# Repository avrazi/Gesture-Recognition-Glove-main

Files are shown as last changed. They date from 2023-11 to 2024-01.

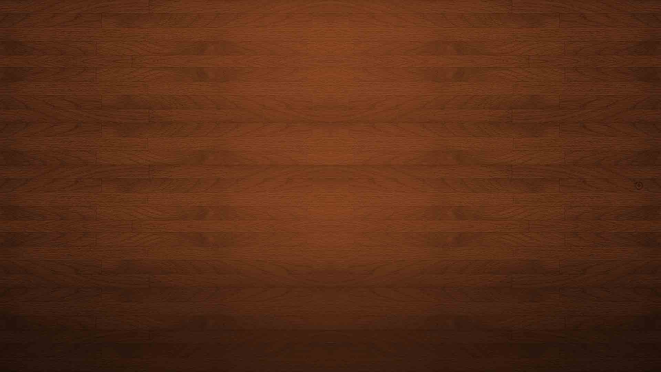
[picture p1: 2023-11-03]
Algorithm/src/wood-backgrounds-wallpapers.jpg

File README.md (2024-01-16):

# Gesture Recognition Glove

*A short intro before starting the article. To anyone who will find themselves reading through this project, please know that, being written around 2020-2021, the algorithm is most likely out-of-date, from the libraries to the dev board used. I've kept everything untouched since then just as some sort comparison for myself a long time ago. Hope it helps!*

***The whole prototype will require 5 flex sensors, a development board, an accelerometer,
gyroscope, and a battery shield.*** During the making of this prototype, a wearable glove will be created
that is **responsive, portable, and durable.** It will be able to translate sign language gestures into readable
form for hearing-impaired people by analysing the bend of the fingers and the position of the hand in
space, process it and send messages to the website. The project started by selecting a suitable
development board, a suitable power supply corresponding the voltage input of this controller, selecting
the right sensors, developing the firmware, designing the PCB and enclosure, and building the prototype.
The PCB will rest along with the battery shield onto a custom-made enclosure. This enclosure will rest
on the back of the hand of the user using a strap keep it tight with the hand and a buckle connecting both
ends of the strap. It will have two straps going on the specified holes. One will be resting above the
thumb and the other strap that connects with a buckle, on the wrist. This will lead for the entire prototype
to not be too close to the fingers, making it a suitable place to make the connection through the
connectors.

The focus of the demo prototype will be on reading and analysing hand movement. Since ASL’s gestures require an extensive range of motions, including rotation and complex arm movement, the algorithm of this prototype will have to be exceptionally well written. It will need to capture correct and consistent analog to digital data to have a precise definition for each value. To bring the proposed design as close as possible to becoming a viable product, there should be a certain required level of standards related to safety to follow. As with any electronic equipment, there is a risk of shorting wires, which can result in injury or fire. This means the points where wires are connected with the Flex Sensors will be fully insulated and the enclosure will have to cover most of the PCB and power supply. Sometimes between gestures, there are very subtle differences and minor changes, so this similarity can be read and
analysed from the glove as the same gesture. The complexity of ASL make it challenging to distinguish
and capture differences between gestures. This means the sensors should have a desired sensitivity and
linearity as well as a well-developed software algorithm that detects these subtle changes. In this case,
we were faced with two options on how to proceed and develop the algorithm. One could be using
machine learning, where the glove would be trained over time by performing the same gestures, or by
creating a dataset function holding if constraints with segments of values. With datasets one gesture
would have exact predetermined values for every sensor reading and would be true if those values would
be met. Deciding which method to choose, and what components to use, we had to make several research
on similar products done beforehand and learn from them.

## Block Diagram

Our next very important step would be to design the block diagram, which will be crucial in the
foundation to the realization of this prototype. The block diagram provides a detailed view and
instructions, making it much easier to understand how every component is related to each other. It is
comprised of the Power supply, Input information, Data processing unit, Data acquisition and the
Website. Starting from the main source of power, the Power supply block (see figure below). It consists of
the battery which supplies the gyroscope, accelerometer, flex sensors and development board. The power
supply in our case will give a +5V as input voltage that goes into the voltage regulator of development
board which will drop it to 3.3V. We can see that the red line represents the input voltage throughout the
circuit. It goes from the microcontroller to the voltage divider of the flex sensor and to that sensor, and
it also connects with the accelerometer and gyroscope module.

Flex sensors will be connected with the microcontroller through an ADC pin and the
accelerometer and gyroscope through a I2C pin. The input information block is where the hand gestures
performed are picked up from the sensors as analog data and fed into the controller. This part only holds
outside factors regarding the prototype. The data given to the controller is processed and analysed
through the algorithm and checked with many datasets. Datasets in our case are going to be numerous if
constraints that hold specific values for when a certain sensor reaches that value. If one of these
constraints if fulfilled, then the output information, which is just a String value, will sent to the opened
webpage through the built-in Wi-Fi module of our development board. From the feeding of the data to
the microprocessor and till the moment this data was sent, it’s called Data Processing Block. In the last
stages of the block diagram, the data sent to webpage, arrives, gets pulled from a function in the
algorithm and is displayed.

The website will display the word, phrase, number, or letter depending on what gesture was
performed from the user of the glove. The information will be displayed as a translated gesture, which
is the goal of our prototype. To get access to this website, the user will have to be connected into the
same Wi-Fi that the board is connected to. By entering this local IP address into a browser of our choice,
we will be directed into the webpage, making the whole process of interaction, simple and efficient. The
website will be sending and giving requests with the board constantly.



#### ***ESP32 Devkit V1***

The ESP32 DevKit V1 is one of the development boards created to evaluate the ESPWROOM-32 module. It is based on the ESP32 microcontroller that boasts Wi-Fi, Bluetooth, Ethernet,
and Low Power support all in a single chip. ESP32 is already integrated antenna and RF balun, power
amplifier, low-noise amplifiers, filters, and power management module. The entire solution takes up the
least amount of printed circuit board area. This board is used with 2.4 GHz dual-mode Wi-Fi and
Bluetooth chips by TSMC 40nm low power technology, power, and RF properties best, which is safe,
reliable, and scalable to a variety of applications. The internal flash of the ESP32 module is organized
in a single flash area with pages of 4096 bytes each. There exist two different layouts based on the
presence of BLE support. Power to the ESP32 DevKit v1 is supplied via the on-board USB Micro B
connector or directly via the “VIN” pin. The power source is selected automatically. The device can
operate on an external supply of 5 to 20 volts. If using more than 12V, the voltage regulator may overheat
and damage the device. The recommended range is 5 to 12 volts. The ESP32 DevKit V1 comes with a
serial-to-USB chip on board that allows programming and opening the UART of the ESP32 module. It
can be programmed in different programming environments like Arduino IDE, Espressif IDF (IoT
Development Framework), MicroPython, JavaScript, LUA.



##### **ADC Reading**

The development board supports 18 ADC channels. Each channel has 12 bits.
So, it has a good resolution. It can be used to measure analog voltage, current and any analog sensor
which provides output in the form of analog voltage. These ADCs can also be used in sleep mode for
lower power consumption. Each ADC channel has a resolution of 12 bits which is equal to: 3.3 / 4095
where 3.3V is a reference voltage and 4095 is minimum step by ADC. This value of 4095 is calculated
from the resolution number of every microcontroller. It is calculated as follows:
212 = 4095.
This means that when we read an analog input, its range may vary from 0 to 4095. Meaning that the
minimum voltage we can measure with these ADC channels is about 80 µV. Anything less than this will
be an error.
Ideally, we expected the ADC readings to have a linear behaviour while using these pins.
However, that is not true. While conducting research on this matter, the opposite was found to be true. We decided to perform an ADC linearity test. Four simple experiments by creating several voltage
dividers to read on. Source was at 3.3V output pin of the ESP32. Then we applied 3 different steps with
4.7k 1% tolerance resistors. These are the values measure with a multimeter:



The results of the Table above have been represented in the chart below. The readings
on the Table above, show when the voltage is at its maximum value, when it’s at ¾ of the maximum value, when
it’s at half and at ¼ of the maximum value. Our thought process was quite simple, as to divide both
voltage and ADC by 4 and have them as references. The most important part on this chart are the
beginning and the end of the characteristic. The behaviour means that our ESP32 cannot distinguish
3.3V from 3.2V. That means we will get the same values of 4095 from both voltages. The same happens
for a very low voltage of 0V to 0.1V. We are getting the same value of 0.



Another problem had arisen from our research that concerned the ADC pins. Specifically
speaking about ADC2 pins. Since our goal is to display our translated gestures using a website, then
the Wi-Fi of the board will be used. We learned that ADC2 pins cannot be used when Wi-Fi is being
used. This means, if we were to use the library of Wi-Fi, we would be getting an error at getting the
values from the ADC2 GPIO. The solution to this problem would be to only connect our flex sensors
with the ADC1 pins which would be GPIO36, GPIO39, GPIO34, GPIO35, GPIO32, and GPIO33.

##### **Voltage Regulator**

The ESP32 has a built-in low dropout voltage regulator chip called AMS1117. In our device,
its servers the function of a 5V to 3.3V linear voltage regulator, which means its main function is to
maintain a steady voltage. The AMS117 is an adjustable and fixed voltage regulator designed to
provide up to 1A output current and to operate down to 1V input-to-output differential. The dropout
voltage of the device is guaranteed maximum 1.3V, decreasing at lower load currents. Current limit is
set to minimize the stress under overload conditions on both the regulator and power source circuitry.
It has 3 fixed pins:

1. Ground
2. VOUT
3. VIN

From our research, we found that there are two versions for the AMS1117. A fixed version and
an adjustable one. Its application circuit is very simple. For the fixed version, it only needs two
capacitors and for the adjustable version only needs two resistors and two capacitors to work. Our
development board uses a fixed output voltage version. AMS1117 has six fixed versions: 1.2V, 1.8V,
2.5V, 2.85V, 3.3V and 5V. For us, we are using ASM1117-3.3, which possesses a
built-in protection against short circuit and thermal overloads. For instance, the circuity-wise thermal
protection will shut-down the linear regulator in case the junction temperature is above 165º C at the
sense point. It provides an output voltage of 3.3V by maximum output current of 1.5A and a maximum
input voltage of 12V. It guarantees a low dropout voltage (input-to-output) differential: VDROPOUT =
VIN – VOUT) of maximum 1.3V at the maximum output current of 1.5A. The dropout voltage decreases
at lower load currents and operates down to 1V dropout voltage. The on-chip trimming develops a
reference voltage of 1.25V between the output and the ground with a reference tolerance of 1.5%. This
means, we have more freedom to choose our power supply in regard to the input voltage required. We have included the electronic schematic of our voltage regulator circuit. It is comprised of 1
220Ώ resistance, 1 LED, 2 capacitors with the same value of 10µF.

##### **Power Consumption**

Since our goal is to build a portable and reliable prototype, we should consider how much does
the ESP32 consumes so we can have a better understand of its lifetime. ESP32 has different power modes
such as:

- Active Mode: The chip radio is powered on. The chip can receive, transmit, or listen.Page |36
- Modem-sleep Mode: The CPU is operational, and the clock is configurable. The WiFi/Bluetooth baseband and radio are disabled.
- Light-sleep Mode: The CPU is paused. The RTC memory and RTC peripherals, as well as
the ULP coprocessor are running. Any wake-up events will wake u the chip.
- Deep-sleep Mode: Only the RTC memory and RTC peripherals are powered on. Wi-Fi and
Bluetooth connection data are stored in the RTC memory. The ULP coprocessor is
functional.
- Hibernation Mode: The internal 8 MHz oscillator and ULP coprocessor are disabled. The
RTC recovery memory is powered down. Only one RTC timer on the slow clock and
certain RTC GPIOs are active.

While we want to have a website open during the whole time the device is on, and the ESP32
will be constantly communicating with the website, the power mode will be stated as ‘Active’. To have a better understanding about the development boards power consumption in an Active
Mode, we will be including a table displaying the RF Power-Consumption Specifications, from the ESP32 DevKit V1 documentation. We can approximate that our power consumption would be 240 mA, considering that we must
keep the development board and website communicating constantly to update the data. The formula to
find the battery life is as follows:
Battery Life (h) = Battery Capacity (mAh) / Device consumption (mA)
For example, if we were to have a battery with the capacity of 2000 mAh, and our maximum
consumption, in ideal conditions, we would have the device running for 8 hours and 19 minutes straight
without interruptions, which is enough for our project.

### Development Board

Regarding the power supply, a suitable battery was searched for to match the input voltage of the
chosen development board. As said before, our ESP32 requires an input voltage of 5V to 12V, so any
battery that has that output is enough for our project. We will be conducting research for rechargeable
battery options because we would like for the lifetime of the prototype being turn on to be as much as
possible without changing the battery. 

Three most common rechargeable battery types include NickelCadmium (NiCd), Nickel-Metal-Hydride (NiMH), and Lithium Polymer (LiPo). Each of these is a good
choice for projects and they all have their benefits and drawbacks. Nickel-Cadmium batteries have a
very high cycle count, and they are typically the cheapest of the three options. However, this type of
battery has a relatively low energy density, so they offer less capacity per cell than the other two types.
On the flip side, NiCd batteries can often deliver very high currents, which makes them perfect for power
tools. Note that NiCd batteries contain toxic heavy metals, which makes them more difficult to recycle.Page |38
Nickel-Metal-Hydride batteries are like NiCd cells. However, NiMH batteries offer an improvement in
capacity over NiCd batteries. One major drawback of NiMH cells is their high self-discharge rate. Li-Po
and Li-Ion batteries have a significantly higher energy density compared to typical NiMH and NiCd
cells. However, this benefit also means that you usually pay more for Li-Po and Li-Ion batteries. Besides
the increased price, lithium batteries always require monitoring by a battery management system, as
these batteries are sensitive to improper handling. Note that Li-Po batteries come in various shapes and
packages, of which some can be very flat. This makes Li-Po cells perfect for handheld devices such as
modern smartphones. Li-Ion batteries often come in larger sizes and are typically used in applications
where size isn’t critical. Note that there is not a single type of Li-Ion or Li-Po battery. Instead, the
category of lithium batteries comprises a whole range of different chemical formulations that all have
their very own pros, cons, and recommended applications.

In our case, a Li-Ion was chosen because they can be recharged many times and are quite stable
and efficient. They tend to have a higher energy density, voltage capacity and lower self-discharge rate
than other rechargeable batteries. This makes for better power efficiency as a single cell has longer
charge retention than other battery types. For the battery to be included and connected with the rest of
the prototype, it should be connected in a certain way. Either through connecting the VIN and GND pins
of the development board or through USB. As mentioned above, our chosen board has a micro-USB
type ‘B’ female. To have a much consistent connection and reliable to connect and disconnect, it was
decided to use a battery shield which will have an USB to make the connection with our board. The size
of this shield should be able to be held on the back of the hand of the user and it should have the option
of being rechargeable. The power supply’s purpose will be simple. It will be connected through USB
type A with the development board with the right input voltage. Since the development board requires
an input voltage of 5 V and has an operational voltage of 3.3V, it will be supplied the exact amount. The
battery shield chosen is the 18650 Battery shield (V3). It was considered for multiple reasons. This shield
is a cheap and portable power supply that can accommodate an ‘unprotected’ single-cell lithium-ion
battery. It also includes a standard USB type ‘A’ female connector, one power on/off switch and a micro-USB
type ‘B’ female for recharging. Its key specifications are as follows:

• Battery charging input: 5V/500mA typical via micro-USB port

• Power supply output: Switched 5VDC via USB type ‘A’ port, 3x 5VDC (VDC= volts
to direct current) (up to 4A) connectors, and 3x3VDC (up to 1A)

• System status indicators: Battery charging and battery charged LEDs

• Battery protection mechanism: Battery overcharge and deep discharge

The background electronics are a clever blend of three requisite circuits a lithium-ion
battery charger circuitry, a battery protection circuitry, and a dc-dc boost converter circuitry. Refer to
the annotated image provided below to get a deep insight on the underlying electronics. In the shield,
the dc - dc boost converter chip is used to deliver 5VDC (4.99V) through the USB ‘A’ socket and 5V
male-header points, generated from the available 3.7V-4.2VDC Li-Ion battery output. The second
channel output, marked as 3V but 3.3V on the dot, is supplied by the parallel combination of three
positive voltage regulator chips. The 3.3VDC supply is derived from the 3.7V-4.2VDC Li-Ion battery
output (not from the 5VDC output)



This device is composed of many components. They will be described by declaring their component
initials which can be check at its Schematic.

- U9 WD01A = Li-Ion battery protection chip
- F1 8205A = Dual N-Channel MOSFET
- U2 TP4056E = Li-Ion battery charger chip
- U7 FP6298 = 4.5A current mode DC-DC boost converter chip
- U4, U5, U6 (XC6206) = Positive voltage regulator chip (3.3V)Page |40
- L1 Green LED = Battery done charging indicator
- L2 Red LED = Battery charging indicator
- S1, S2, S4 = Schottky Diodes



### Flex Sensor

Capturing the bend of the fingers could be done in very few ways. Judging from the research
conducted beforehand on similar projects, flex sensors proved to be a good and efficient way of
measuring the bend of the fingers. Our options regarding the decision on acquiring the right flex sensor
for our prototype were limited. Generally, there are 3 main types of flex sensors: Conductive ink-based
flex sensors, fibre optic flex sensors and capacitive flex sensors. The conductive ink-based flex sensors
are quite common for projects of this nature. Capacitive and fibre optic flex sensors can be used more inPage |41
industrial and professional equipment. Conductive ink-based flex sensors are unipolar sensors, which
means the change of resistance is true only if you bend it in one direction. Bending the sensor on the
other direction does not change its resistance. It uses conductive ink whose resistance varies when bent.
The ink may contain carbon or silver to make it conductive. The spacing between carbon particles are
lager when bent and close when straight which results in a change of resistance.
Regarding the purchasing options, there were only two. 2.2 inches and 4.5 inches flex sensors
were available. 

Five 4.5 inches flex sensors were purchased instead of the 2.2 inches because they better
match the length of the fingers. The main computing device is going to be used to configure input and
output pins for each sensor, setup a clock speed, configure communications with the ADC, configure
communications with I2C pins, control sensor data, and send valid data to a Wi-Fi module. Flex Sensors
will be manipulated in the algorithm to decide whether the finger will be closed, open or to determine
exact positions for them.

##### **Power Consumption**

Each Flex Sensor is treated as a variable resistor whose resistance increases which the sensors
bending. Each sensor constitutes a part of its own voltage divider circuit, whose output is processed
through one of the development board’s analog-to-digital converters. The voltage provided from the
controller will be changing because of how much the corresponding finger is bent, which can lead to
problems while using the device. More specifically speaking, if the flex sensor would be changing its
value, the voltage would do as well. To fix this issue, voltage dividers will be placed before the Flex
Sensors. Voltage divider’s purpose in this case is to supply analog voltage values from
divider central point where both two resistors are connected. Voltage dividers only divides power
supply voltage value in proportion of Resistors values. One resistor has fixed value other value is
changing. Imagine two values are equal. Then voltage will be divided by 2.



The flex sensors were measured using a multimeter to determine their values. We agreed to set
the resistance when the sensor is straight as 12.3kΏ and for when it’s bend at 180º, it’s 29kΏ. By
connecting the sensor to a voltage divider circuit, the resulting voltage can be calculated from the
formula:



So, if we wanted to find out the output voltage, taking the flex sensor when it is straight and the
power supply voltage of 3.3V, according to the formula, it would be equal to 1.47V and for when we
are calculating for when flex sensor is bent, we get 0.846V.



Now, to find the current consumption of each flex sensor we would use this formula:



We can see that the circuit consumes very little current making it an energy efficient circuit,
considering that the board will reach around 240mA as consumption. This makes the use of the 10kΏ a
good value to choose for the voltage divider.
Regarding the value of voltage that will serve as an indicator for us to know if the flex sensor has
been bent, we decided that bending the sensor 90º (see Figure 24). This means that we can calculating
the resistance at half-way to our maximum bend value of 180º. This resistance is equal to:

29000Ώ – 12300Ώ = 16700Ώ.
16700Ώ / 2 = 8350Ώ.
12300Ώ + 8350 Ώ= 20650Ώ

We can calculate the voltage of this threshold as follows:



From our results we can understand that the voltage of 1.07V will be understood as a bend in the
flex sensor with that value.

### Accelerometer and Gyroscope

Regarding both accelerometer and gyroscope, the idea was based on the solution in Review 1,
where the team was using a MPU6050 module which contained both an accelerometer module and a
gyroscope module. It combines a 3-axis gyroscope and a 3-axis accelerometer on the same silicon die
together with an onboard Digital Motion Processor (DMP) capable of processing complex 9-axis
algorithms. This will help us to measure acceleration, velocity, orientation, displacement, and many
other motions related parameter of the prototype. The price of this is 5.5€ which made it a very
reasonable and efficient option for the realization of our prototype. It is comprised of 5 pins, INT, SCL,
SDA, GND and VIN. 

The INT is the interrupt signal which is an optional pin to connect. It indicates that
data is available for MCU to read. SCL stands for Serial Clock and is used for providing clock pulse for
I2C communication. SDA means Serial Data and is used for transferring data through I2C
communication. VIN will provide the power for this module, can be +3V to +5V depending on the added
power supply. In our case, the power will supply 5V into the board. GND stand for ground and connected
the system to ground. The main features or the MPU6050 are:

• MEMS 3-axis accelerometer and 3-axis gyroscope values combined,
• Power Supply: 3-5V,Page |44
• Communication: I2C protocol,
• Built-in 16-bit ADC provides high accuracy,
• Built-in DMP provides high computational power,
• Built-in Temperature sensor.

A gyroscope to capture the orientation and the angular velocity of the hands. Gyroscope will prove
useful for certain gestures that will require rotary movement in space. Accelerometer will be used to
measure the acceleration of the hand, which will be useful for gestures of phrases or words that need
stretched movement of the hand in space.



## Schematic Diagram

The first step taken for the realisation on this prototype was to design the schematic by placing
the components on a simulated breadboard to have a clearer view of how everything would be connected.
This proved to be quite helpful as a step before placing the components a real breadboard and start
experimenting. was designed using Altium Designer. This would
prove very useful, because the schematic would be imported easily for the next step of creating the PCB
using the same software. In the schematic, we can see how the components are connected with each
other. The flex sensors are shows as variable resistors with the names of Flex 1, Flex 2, Flex 3, Flex 4,
and Flex 5. Each sensors had their resistances measured beforehand to decide their value without any
force put into. This proved an approximated value of 12kΏ. Each of these sensors is connected to their
own voltage divider. These resistances have been assigned a value of 10kΏ. Each flex sensor has been
connected to an ADC pin of the ESP32. These pins are GPIO34, GPIO 35, GPIO 33, GPIO 32 and
GPIO39. We can also see in the schematic design that the MPU6050 module is connected without
development board as well.



The ESP32 has 6 Analog-To-Digital pins assigned as ADC1 and 9 Analog-To-Digital pins
assigned as ADC2. Since our goal is to send the data gathered to an opened webpage, this means that
the flex sensors would be able to connect to ADC1 pins only. From the schematic, we can
also see that the MPU6050 module is connected with the board to the specified pins. In the Pinout Figure
of the ESP32, we can see that GPIO21 and GPIO22 have the following names assigned: I2C SDA and
I2C SCL respectively. Therefore, they are connected to the pins of the same names of the module. Every
VIN pin has been connected and so has the GND pins. It is displayed that the input voltage of the circuit
will be 3.3V as is the operating voltage of the development board. The 18650 battery in-use are the
18650 US18650VTC4 Li-Ion 3.7V 2100mAh 30A. 

The ESP32’s lifetime on battery power has not been
tested, but as an approximation it could last around 4 months without charging the battery. Since the
board will be awake, it will need to be on during the whole time. Our main objective is to enable the user
of the glove to be able to fully communicate with another person through the use of a website, which
will serve as a lobby where anyone can connect with. This website will be run on the development board
at the same time it is reading the sensor data. As long as the user of the glove has a mobile phone and
internet mobile data, it will make the communication much easier. They will be taken to a specific IPPage |47
address where this webpage is opened. This was an option we explored as a very efficient one, amongst
other options. We could have developed an easy-to-use mobile application that would’ve performed the
same tasks, but it opened the way to new problems. Such as for what reason would someone download
this app, taking into consideration the chances a person has to meet someone with a hearing impairment.
Even if they did, it would’ve made it more difficult to get the message across to download it in order to
communicate. How would someone know the existence of this app? What if in an extreme situation,
there was a need for the interaction of a person and a hearing-impaired person? What if the person who
will need to get the app does not have enough internet to download it? All these obstacles made the
development of an app obsolete, as it would lead to more headaches and annoyances throughout the
daily life. We decided to research on this matter as well as it is very important how we will be displaying
the translated gesture.

## PCB Design

From the schematic design, all the connections, components and names of components have been
imported to create the PCB of this prototype. The PCB was designed while have the enclosure design in
mind. This means that to properly design the PCB, the dimensions should’ve have been decided before
creating it. Therefore, the dimensions of this PCB are 70x50mm. According to the design of the
enclosure, the longest part would be placing the 18650-battery shield which would be very near the PCB.
The PCB’s dimensions resemble the back of the hand, from the end of the wrist till the beginning of the
fingers. PCB has two layers, a top and bottom one. It has a top and bottom overlay with the name of the
author and its logo and the logo of the university on the back. 4 mounting holes have been put on the
four corners with the sizes of 2.5M screws. Every resistor has their name on the top overlay, just like the
development board and MPU6050 module. The PCB has a common ground, which means the ground
pins are not connected through route connections but go through the same layer. This is a very effective
tool to minimize the routes through the PCB, making less chaotic. Via stitching was used to tie together
large copper areas on different layers to create a strong vertical connection through the board structure.
This helps maintain a low impedance and short return loops. The width of the board was decided to be
a standard 1.6 mm. The PCB was designed and ordered through PCBWay, and it arrived surprisingly
quick, in around 5 days. When ordering our PCB, Gerger Files were generated and the Drill Holes files
that are necessary for the manufacturing and development of our PCB.





The resulting PCB that was ordered and shipped. PCB was ordered twice. The first time’s
resulting PCBs had two main mistakes. The place where the MPU6050 would be soldered into, was too
close to the development board and Flex sensor 5 was connected with the wrong the ADC pin of the
board. It was connected to a ADC2 pin, the ESP32’s ADC2 pins
cannot be used while using the Wi-Fi module. Redesigning the PCB, the stitching holes were kept the
same. The holes for the MPU6050 have been moved up by 3 mm leaving more space for it and the Flex
Sensor 5 was connected with GPIO 39 of the ESP32.

## Software Framework

After designing the PCB, we put our attention to create a very efficient algorithm that would
gather data, analyse them, process them, check them, open a website, create a webpage, and update the
values. In this chapter, we are going through the Software Framework, which explains the logical idea
of the whole algorithm. From the extensive research, it was decided that the prototype will be working
using a dataset in its algorithm, discarding completely the idea of including machine learning. We will
be exploring the ESP32 and its entire capabilities while focusing on speed of transmission of data.
The framework starts from booting the microcontroller. As soon as it
is turned on, it will initialize the Accelerometer and Gyroscope sensors. This means, a function will
perform a checking statement to verify whether MPU6050 is connected or not. If it’s not, then the
MPU6050’s LED won’t turn on. In this situation the main board can be restarted by pressing the EN
Button. If the problem is persistent, then this means there is a problem with the connection between the
main board and the sensor module. This explains the significance to this simple function that is critical
to the communication between the device and the user as it indicates the state of functionality. It is very
important to have visual representation of the status of the device the user is using. This function is one
of the few functions that were added to serve as debugging functions in case problem would arise.
Whenever the board is booted, a red LED is turned on to indicate it. 

The next part is calibration of the
flex sensors. Here the user has 15 seconds from the boot of the board to open and close their fingers to
calibrate the flex sensors values. The ESP32s ADC pins gathering of data fluctuate extensively, with the
values changing for the same position of the finger every time the board is booted. This proved that the
specified maximum and minimum values of flex sensors resistance would be incorrect. The
measurements would be less than the minimum and more than the maximum than the measurements
conducted with a multimeter for each flex sensor. Calibrating the flex sensor would give each flex sensor
their individual maximum and minimum, balancing out the values differently each time the board would
boot. 

After taking care of every sensor the prototype has, the next step would be to open the website.
The board has been given specific credentials to connect to a Wi-Fi in its surrounding. It will scan the
area and if it finds the same name of the router or switch device, it will connect to it, putting in the
password provided as well. In this stage, the board has successfully initialized a Transmission Control
Protocol (TCP) server. This is a connection-oriented communication protocol that facilitates the
exchange of messages between computing devices in a network. If the server has been initialized, then
the board connects to it. From experimenting, it has happened that the device may not find the specified
Wi-Fi, or there may be a problem with the transmission of the Wi-Fi. This issue leads to the device not
being able to connect to the Wi-Fi and the website cannot be open successfully. In the case where the
connection is successful, the board opens the website. This concludes the setup part of the algorithm,
which is displayed to the user with a blue LED turning on, indicating that the glove is ready to be used.
In the case explained beforehand, where the website would not connect properly, the user could not see
the blue LED after the roughly 15-16 seconds from booting the board. This can be fixed by manually
pressing the restart button EN. The next part is conducted in the loop function of the board. It starts with
the gathering the data from each individual sensor. 

There is a specific function for data of accelerometer,
one for gyroscope and one for flex sensors. Each of these functions is called in the loop function. The
values gathered are checked with the constraints of the dataset, which itself is its own function. Datasets
are if constraints that hold specific values for every sensor and are equal to one specific word, number
letter or phrase. When one of these if constraints is fulfilled, they send a string value with the right result.
This result is sent to the webpage and gathered there where it would be displayed as a translated gesture.
So, since the webpage remains open indefinitely until the user restarts, or the device is disconnected
from the Wi-Fi. If new data was not received, then nothing would change in the webpage displaying the
translate gesture. This was managed through a function that makes the current displayed gesture as
‘current reading’. Since we know that the loop function keeps running indefinitely, the displayed gesture
would print every half a second. This function will display the next gesture when another constraint is
fulfilled, naming it as ‘new gesture’. So, this constant loop will keep reading new values, checking with
the datasets, and updating whenever gestures change, reaching our desired goal.



## Enclsoure Design

To design the enclosure, the PCB dimensions were taken into consideration. The idea behind the
enclosure is to build a sturdy box that would hold both the power supply and development board. It is
going to have an upper side and a lower side. With the
already mentioned specifications on what our goal is, the enclosure will have 2 openings on the eastern
side, for the USB type A of the 18650-battery shield and one for the micro-USB type B of the ESP32.
Two smaller openings would go on the southern side, where the smallest would be for the switch that
the battery shield has and the bigger one would be for the micro-USB type B which will be used to
charge the battery inside. Since our prototype requires a certain level of conveying stages of functionality
to the user along with the restart button EN being a crucial part when a problem would arise, an opening
would be positioned on top of the development board. This opening would cover the two LEDs and
make it possible for the user to manually press the restart button EN. One other opening on the top side
is going to be positioned on top of the flex sensor markings. This will leave space for the connectors to
be soldered onto the PCB and they will be as high as the enclosure. This will protect them from outside
factors or accidental pushes. Enclosure was designed with a logo to give it a more personal touch and
serves as a branding mark. It will have two smaller opening it the thickest side, the nearest with the
battery shield, one to recharge the battery using a micro-USB type B, and the other opening will be used
for the switch, to turn the battery on or off. The opening for charging has the dimensions of 5x5mm and
the opening for the switch has the dimensions of 4x4mm. To have the enclosure sit on the back of the hand, we designed it in a way that it could be strapped
onto the hand. This was done through two holes on both sides where a strap with the width of 2mm
would go inside and around it, connecting with a buckle. The idea was inspired from professional digital
photographing equipment that are carried around strapped onto the user’s neck. The furthest holes,
furthest away from the battery shield, would be connected around with a strap, without the need of a
buckle. This would serve only as s supporting strap that will stand above the thumb. The other hole
would be connected together using a buckle that would make the connection around the wrist. This way,
the enclosure would stay and rest in place without moving while the user is performing gestures.
Mounting holes for 18650 battery shield and PCB support 2.5M screws and the lower lid can be mounted
using holes supporting 3M screws. The design was made using Autodesk’s Fusion 360 and SolidWorks.
The thickness of the walls has been put as 2mm across the whole device. The real model was 3D printed
and mounted together with the other components. Results of the design have been displayed.





## Results and Testing

The nature of this PCB, required movement of the board in many directions, making it harder to
solder components. It was accomplished from the help of ‘Flexible Helping Hands Soldering Station’.
This station made it much easier to solder the connectors and the MPU6050 chip, which proved to be
harder to keep in place to solder. Soldering iron used has been displayed for full disclosure in Appendix
5. It was equipped with a conical tip for greater precision during most of the soldering process, and a
bent tip for the development boards pins since they are quite close with each other. The soldered resulting
PCB has been shown below:



Regarding the printing of the enclosure, both upper and lower lid have been 3D printed. Since the upper lid is a
complete opened area, a lot of supporting fibres were added inside it entirely covering the empty spaces.
These supports would be cut out after it had been printed entirely. This was added to not have the printing
fail. The printing of the upper lid took roughly 12 hours and for the lower lid, around 2 hours. Both were
printed successfully with the first try, so there was no need for more printing.



As it was mentioned during the Enclosure Design, the lower lid has mounting holes for M3
screws. M3 nylon screws have been used to mount up the lower part unto the upper part. For the PCB,
it is needed 2.5M screws. PCB was placed carefully onto the holes, while taking care of the connectors
of flex sensors to pop out from the opening specified. Battery shield has been mounted in the
corresponding place using 2.5M screws, just like the PCB. Results of mounted components has been displayed.



Regarding the glove, flex sensors have been placed into each finger. Two 5mm cuts were made in each
finger, with a 1mm to 2mm distance from the first cut, depending on the length of the finger. The idea
was to make a path for the sensor so it would be harder for it to fall off the glove. The cloth material
definitely helps with friction, making it impossible for the
sensors to fall away. These sensors go around and inside these
cuts, making them like going in and out small pockets, and
appearing only by a bit outside of the glove, on these pockets.
Each of them, has been cold soldered with the male header
pins of the PCB connectors. This way we have concluded in creating
the enclosure and glove. After connecting the enclosure and the flex sensors on the glove, the strap and buckle were
prepared. Both sides of connecting straps have been sewed for greater grip on the hand. The final
completed prototype is shown below.





After finishing the mounting and creating the prototype, we continued to test. This means we
would start and test the functionality of the algorithm. Many gestures have been implemented into the
prototype. For the time being, the glove can translate number 1, 2 3 and 4. It can say the phrases ofPage |68
‘Hello!’ and ‘I love you!’. It can say the words ‘My’, ‘Name’ and it can translate the letters ‘T’, ‘E’, ‘D’
and ‘I’. The next set of figures will be a representation of our work, displayed with a proof of hand
gesture, website reading and a representation of the real gesture in ASL.





## Summary of work results

After testing our prototype, we can safely say that we have reached our goal of developing a
responsive, portable, and durable device. The website works as intended and as designed. It gathers and
translates the gestures performed in real time. We have displayed many phrases, words, numbers, and
letters. The entire project was started from an idea. An idea that was stated as a solution to a problem. It
was intended to solve the difficulty gap between hearing-impaired people and the hearing world, by
making their daily life safer and easier. It was meant to surpass the designs of previous projects.
The process started by building a block diagram, deciding what relationships the many devices would
have with each other. It continued into much extensive research about similar works previously made,
which made the idea clearer. This way we could decide which roads to undertake without spending our
time exploring many ideas.

We constructed the schematic design using the components along adapting each of their parameters
with each other. That step made the building and designing the PCB much easier by importing the already
done assets onto Altium Designer. The PCB was made while having in mind an idea for the enclosure.
Algorithm was developed in a quite simple manner, with many void functions, by making the whole
code readable to anyone and efficient. This way, we could focus on performance issues, small fixes on
the datasets of gestures, and adding more gestures as features. The data was uploaded in a JSON variable
into our Asynchronous server. Enclosure was built later, which was the most challenging part of this
whole project. It required many trials and errors.

Many problems arise on designing the openings for the battery shield and the PCB. Looking at the
work in a more critical point of view, the opening for the on/off switch of the battery shield could be a
couple more millimeters bigger on both dimensions, and so could the opening for the charging microUSB type B. Using SolidWorks for the enclosure proved quite useful because the design was done part
by part. Each component was designed separately to have a better picture of the idea. The testing revealed
many smaller defects of the prototype. The wires can be insulated for a more professional look. The flex
sensors inside the glove could have been sewed for a better grip, leaving room for smaller improvements.
After the implementation, the device meets its intended requirements and objectives, while achieving
every goal set at the beginning of this project. The designed device is extremely simple in construction,
both in PCB, enclosure, making it a reliable product with a low-cost production.

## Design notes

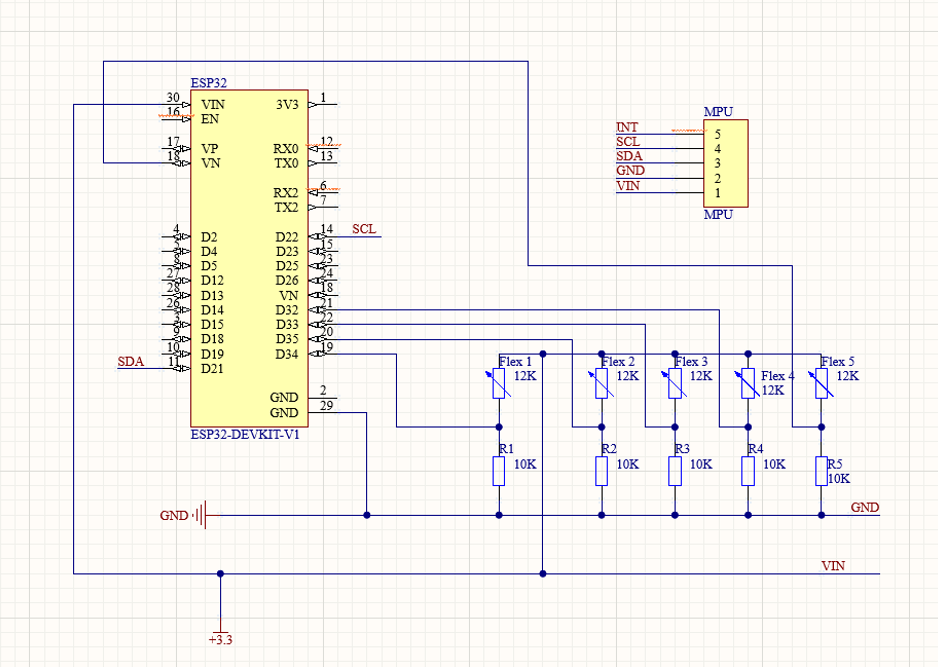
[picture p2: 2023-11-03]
Schematic Diagram.png

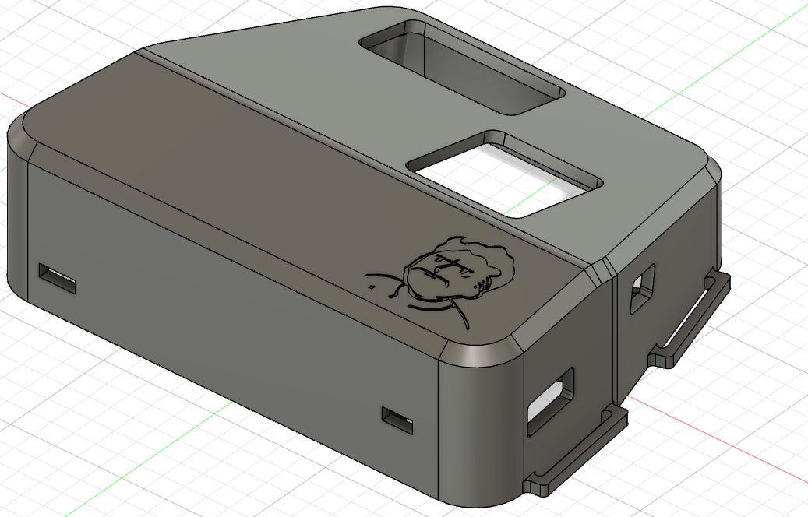
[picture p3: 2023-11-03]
Enclosure/Images/Upper lid.png

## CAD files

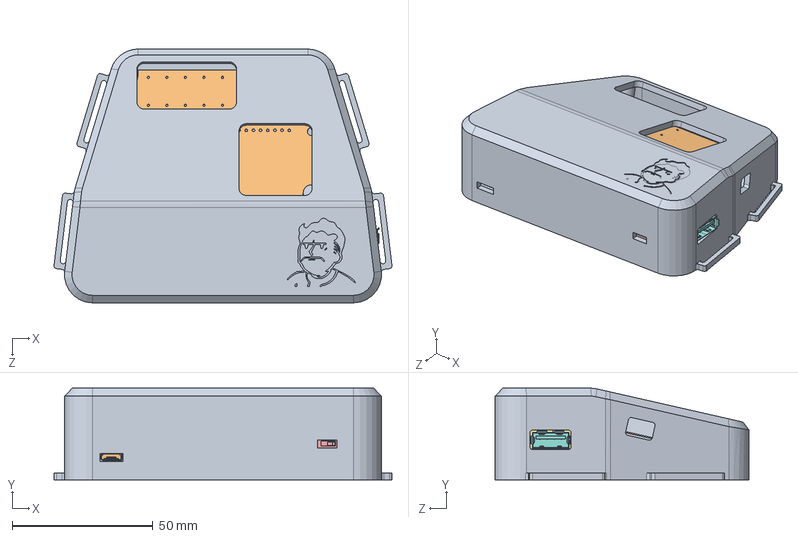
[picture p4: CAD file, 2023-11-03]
Enclosure/Source File/Assem7.SLDASM
119.9 x 32.5 x 90.0 mm
shield.step
socket_housing.step
socket_plate.step
terminal.step x 5
Placa.step
PANASONIC_NCR-18650B.step
Battery Holder.step
Female USB.step
Enclosure Flex
PCB11_VZ.step
Lower Lid

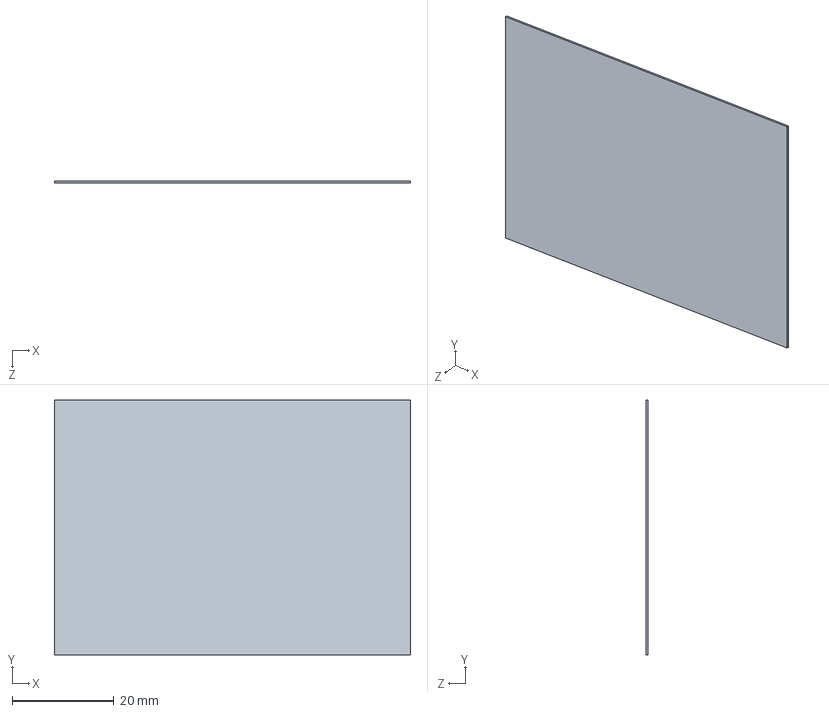
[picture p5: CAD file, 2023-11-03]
Enclosure/Source File/PCB.step.SLDASM
70.0 x 50.0 x 0.411 mm

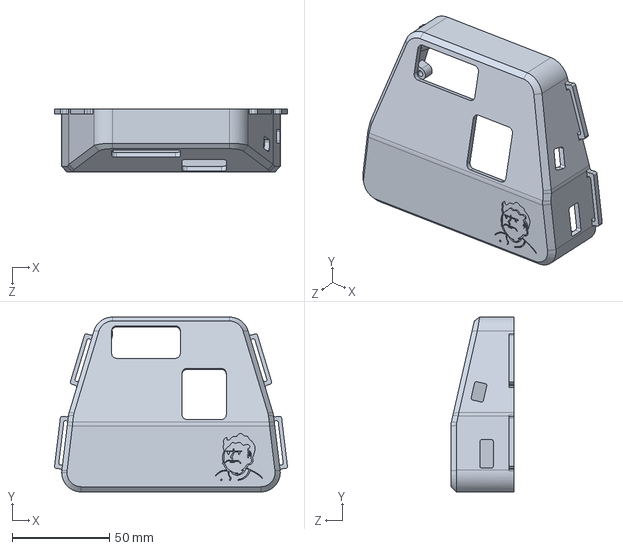
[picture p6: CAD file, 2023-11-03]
Enclosure/3D Printable File (STL)/Upper Lid Modified/Upper Lid Modified.STEP
119.9 x 90.0 x 32.5 mm

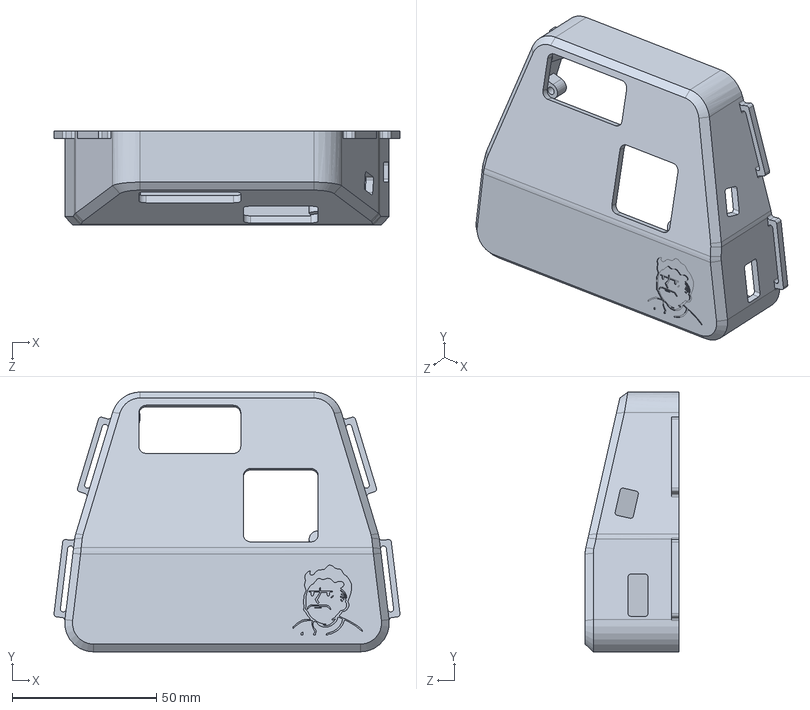
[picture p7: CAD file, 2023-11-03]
Enclosure/Source File/Enclosure Flex.SLDPRT
119.9 x 90.0 x 32.5 mm

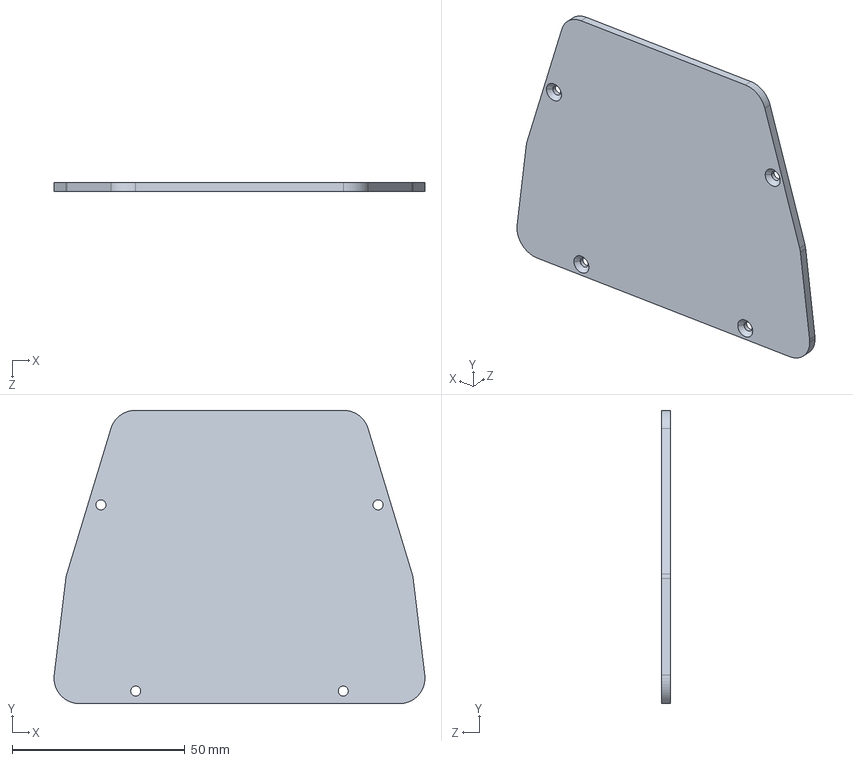
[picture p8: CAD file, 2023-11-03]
Enclosure/STEP Format/Lower Lid.STEP
107.2 x 84.8 x 2.50 mm

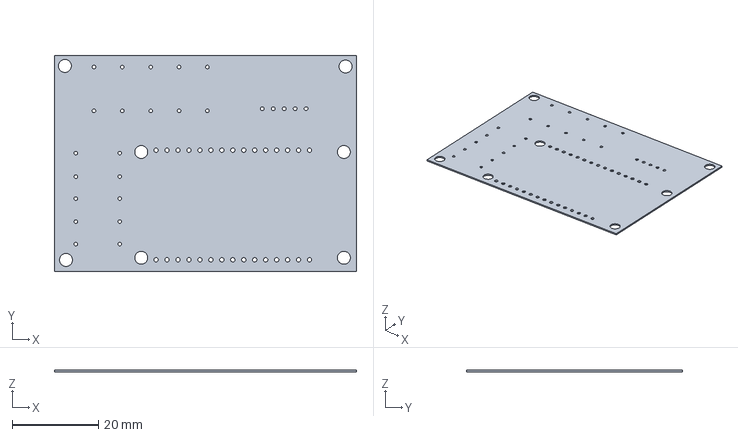
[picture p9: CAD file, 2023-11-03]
PCB/PCB/PCB.step
70.0 x 50.0 x 0.411 mm

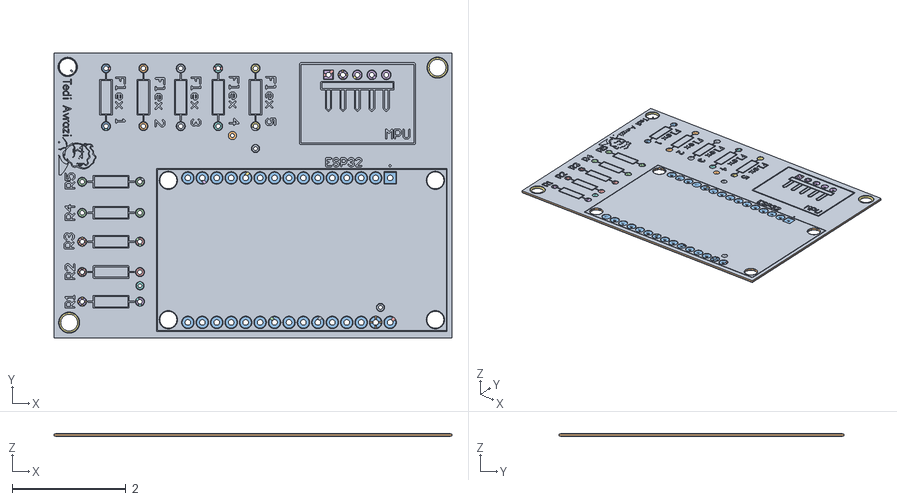
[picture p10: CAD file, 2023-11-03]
PCB/PCBToBeBuiltOn.obj
7.00 x 5.00 x 0.0564
Top
Bottom
ESP32
R5
R2
MPU
Flex 5
Flex 4
Flex 3
Flex 2
Flex 1
R4
R3
R1
NetFlex 2_1
NetFlex 5_1
GND
NetFlex 4_1
NetFlex 3_1
VIN
SCL
SDA
NetFlex 1_1
Solder_Top
Core
Solder_Bottom

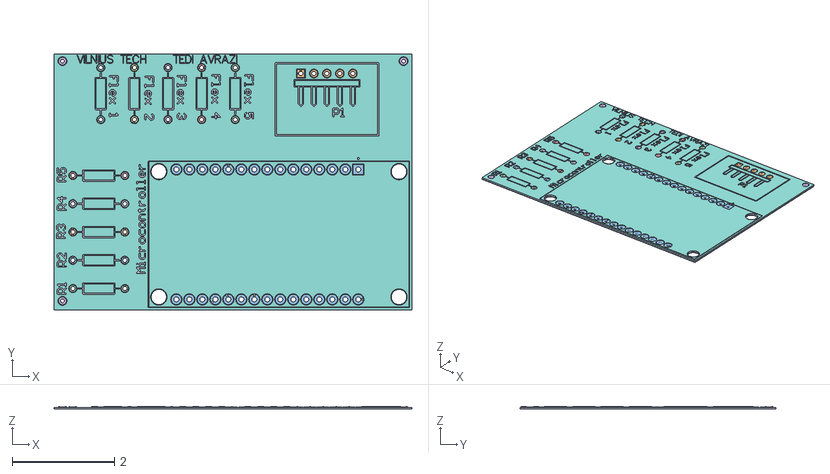
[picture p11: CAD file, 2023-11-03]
PCB/PCB of Thesis.obj
7.00 x 5.00 x 0.0528
Top
P1
Microcontroller
Flex 5
Flex 4
Flex 3
Flex 2
Flex 1
R4
R3
R2
R1
R5
NetFlex 3_1
NetFlex 4_1
NetFlex 2_1
SDA
SCL
VIN
NetFlex 5_1
NetFlex 1_1
GND
Solder_Top
Core
Solder_Bottom

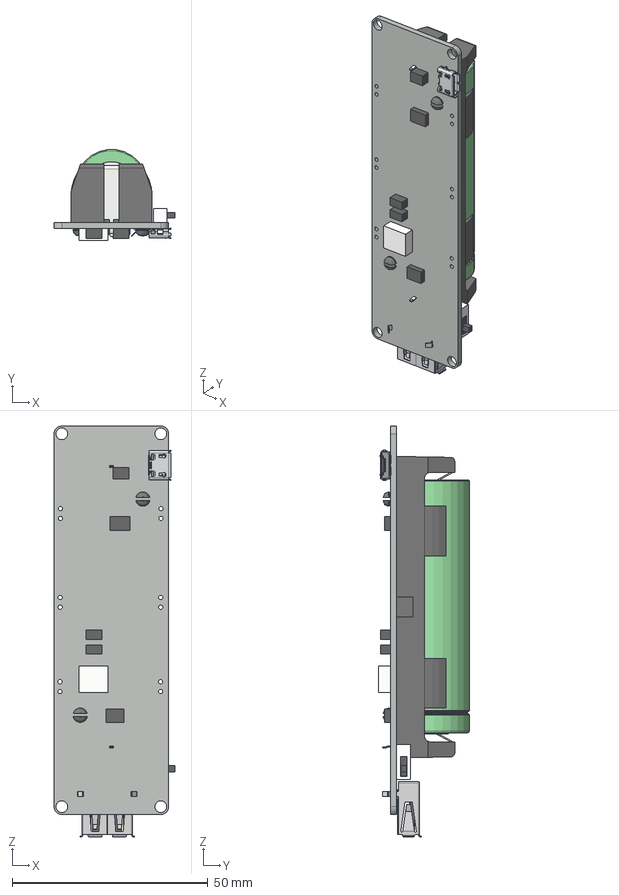
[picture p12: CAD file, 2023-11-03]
Enclosure/Source File/Wemos Battery Shield V3.step
30.9 x 23.2 x 105.0 mm
Placa
PANASONIC_NCR-18650B
Battery Holder
Female USB
shield
socket_housing
socket_plate
terminal x 5

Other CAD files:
Enclosure/Source File/Board.step.SLDASM
Enclosure/Source File/STEP_[No Variations].step.SLDASM
Enclosure/Source File/Open CASCADE STEP translator 6.8 1.1.1.step.SLDPRT
Enclosure/STEP Format/Upper Lid.STEP
Enclosure/Source File/PCB11_VZ.step.SLDPRT
Enclosure/Source File/Lower Lid.SLDPRT
Enclosure/Source File/STEP_[No Variations].SLDPRT
Enclosure/Source File/Upper Lid.SLDPRT
Enclosure/Source File/Fillet2.SLDPRT
Enclosure/3D Printable File (STL)/Lower Lid.STL
Enclosure/3D Printable File (STL)/Upper Lid Modified/Upper Lid Modified.SLDPRT
Enclosure/3D Printable File (STL)/Upper Lid Modified/Upper Lid Modified.STL
Enclosure/3D Printable File (STL)/Upper Lid.STL
Enclosure/Source File/CSK for M2.5 Flat Head Machine Screw1[1].SLDPRT
Enclosure/Source File/Enclosure Assembly Drawing.SLDDRW
Enclosure/Source File/Wemos Battery Shield V3.SLDASM

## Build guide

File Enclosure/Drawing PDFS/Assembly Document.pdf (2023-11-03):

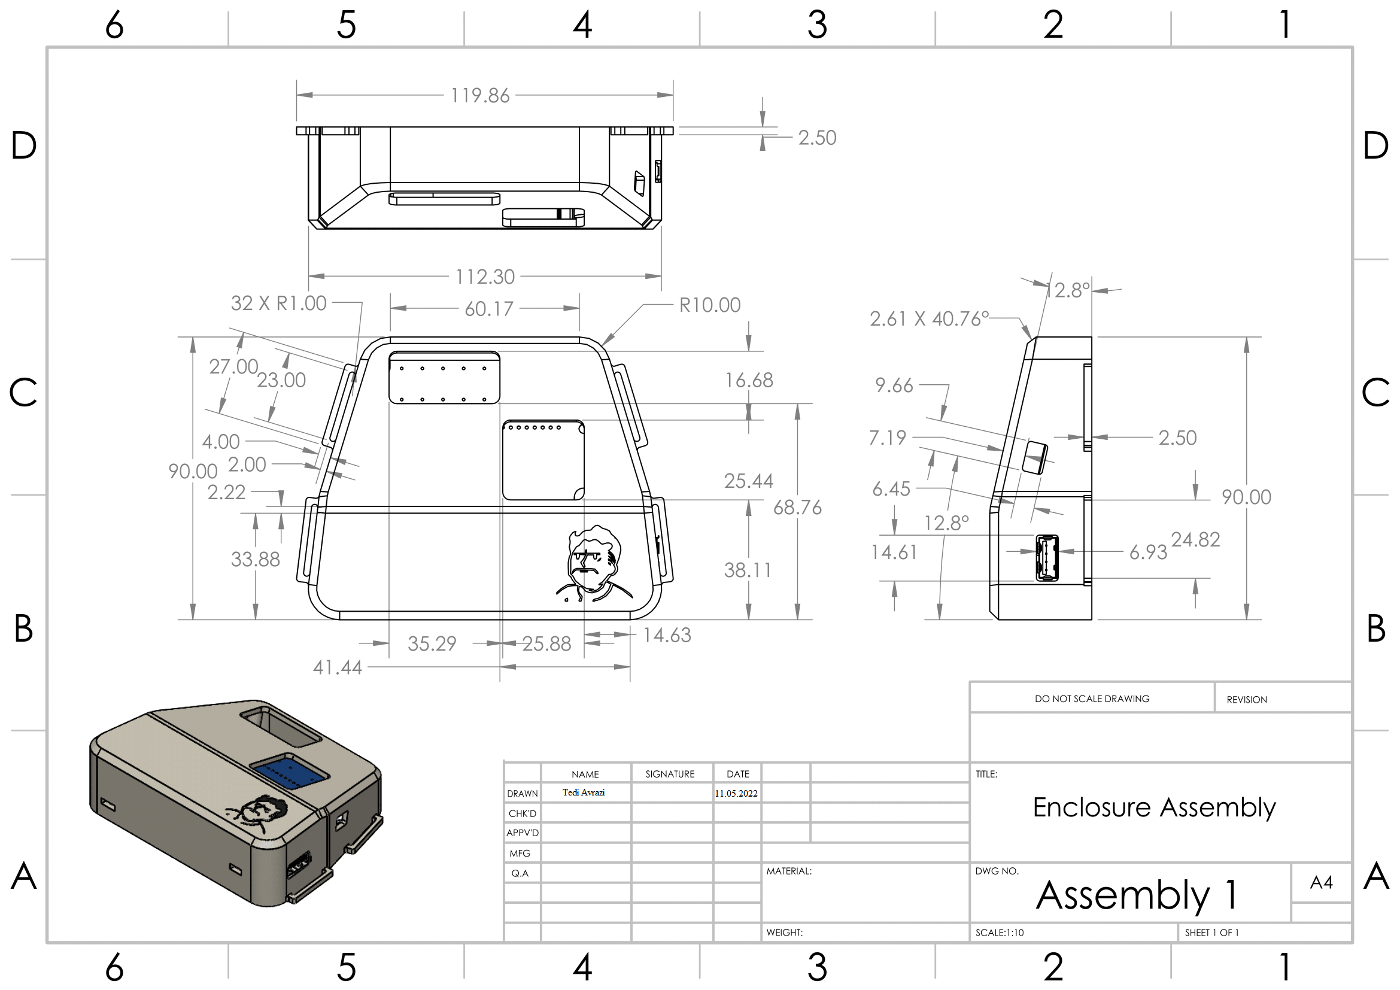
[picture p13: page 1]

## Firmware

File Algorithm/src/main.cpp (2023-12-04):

/************************************************************************/
/*                          Libraries                                   */
/************************************************************************/
#include <Arduino.h>
#include <Adafruit_MPU6050.h>
#include <Adafruit_Sensor.h>
#include <WiFi.h>
#include <WiFiClient.h>
#include <WebServer.h>
#include <index.h>
/************************************************************************/
/*                          Variables                                   */
/************************************************************************/
// Create a Asynchronous Web Server object on port 80
WebServer server(80);
// Network Credentials 
const char *ssid = "Wi-Fi name";
const char *password = "Wi-Fi pass";

#define LED 2

// Variables
const int Flex_Sensor1 = 34;
const int Flex_Sensor2 = 35;
const int Flex_Sensor3 = 33;
const int Flex_Sensor4 = 32;
const int Flex_Sensor5 = 39;
const float VCC = 3.3;
const float R_Divider = 10000.0;

float R_Straight1 = 12300.0;
float R_Bend1 = 29000.0;
float R_Straight2 = 12300.0;
float R_Bend2 = 29000.0;
float R_Straight3 = 12300.0;
float R_Bend3 = 29000.0;
float R_Straight4 = 12300.0;
float R_Bend4 = 29000.0;
float R_Straight5 = 12300.0;
float R_Bend5 = 29000.0;

float flexV1 = 0.0;
float flexR1 = 0.0;
float flexV2 = 0.0;
float flexR2 = 0.0;
float flexV3 = 0.0;
float flexR3 = 0.0;
float flexV4 = 0.0;
float flexR4 = 0.0;
float flexV5 = 0.0;
float flexR5 = 0.0;

String storeReadings = "";
String OldstoreReadings = "0";

// Accelerometer and Gyroscope Variables
unsigned long lastTime = 0;
unsigned long lastTimeAcc = 0;
unsigned long gyroDelay = 10;
unsigned long temperatureDelay = 1000;
unsigned long accelerometerDelay = 200;
float gyroX, gyroY, gyroZ;
float accX, accY, accZ;

// Creating an object for the MPU6050
Adafruit_MPU6050 mpu;
sensors_event_t a, g, temp;

// Gyroscope sensor deviation
float gyroXerror = 0.09;
float gyroYerror = 0.04;
float gyroZerror = 0.02;
/************************************************************************/
/*                        Initialization of MPU                         */
/************************************************************************/
void initMPU()
{
  if (!mpu.begin())
  {
    Serial.println("Failed to find the MPU6050 chip.");
    while (1) 
    {
      delay(10);
    }
  }
  Serial.println("MPU6050 was found!");
  Serial.println("\n");
}
/************************************************************************/
/*                       Initialization of WiFi                         */
/************************************************************************/
void initWiFi()
{
  WiFi.mode(WIFI_STA);
  WiFi.begin(ssid, password);
  Serial.println("");
  Serial.print("Connecting to WiFi");
  while (WiFi.status() != WL_CONNECTED)
  {
    Serial.print(".");
    delay(1000);
  }
  Serial.println("\n");
  Serial.println(WiFi.localIP());
}
/************************************************************************/
/*     This routing is executed when you open its IP in browser         */
/************************************************************************/
void handleRoot()
{
  String s = index_html; // Read HTML contents
  server.send(200, "text/html", s); // Sends the Web Page
}
/************************************************************************/
/*                   Calibrating the flex sensors                       */
/************************************************************************/
void Calibration()
{
  Serial.println("Starting Calibration.\n");
    while(millis()<15000)
  {
    float Flex_Value1 = analogRead(Flex_Sensor1);
    float Flex_Value2 = analogRead(Flex_Sensor2);
    float Flex_Value3 = analogRead(Flex_Sensor3);
    float Flex_Value4 = analogRead(Flex_Sensor4);
    float Flex_Value5 = analogRead(Flex_Sensor5);
    
    if (Flex_Value1<R_Straight1)
    {
      R_Straight1=Flex_Value1;
    }
    if(Flex_Value1>R_Bend1)
    {
      R_Bend1=Flex_Value1;
    }

    if (Flex_Value2<R_Straight2)
    {
      R_Straight2=Flex_Value2;
    }
    if(Flex_Value2>R_Bend2)
    {
      R_Bend2=Flex_Value2;
    }

     if (Flex_Value3<R_Straight3)
    {
      R_Straight3=Flex_Value3;
    }
    if(Flex_Value3>R_Bend3)
    {
      R_Bend3=Flex_Value3;
    }

     if (Flex_Value4<R_Straight4)
    {
      R_Straight4=Flex_Value4;
    }
    if(Flex_Value4>R_Bend4)
    {
      R_Bend4=Flex_Value4;
    }

    if (Flex_Value5<R_Straight5)
    {
      R_Straight5=Flex_Value5;
    }
    if(Flex_Value5>R_Bend5)
    {
      R_Bend5=Flex_Value5;
    }
  }
  Serial.println("Calibration was successful.\n");
  delay(400);
}
/************************************************************************/
/*                   Gathering data of Gyroscope                        */
/************************************************************************/
void getGyroReadings()
{
  mpu.getEvent(&a, &g, &temp);
  float gyroX_temp = g.gyro.x;
  if(abs(gyroX_temp) > gyroXerror)
  {
    gyroX += gyroX_temp/50.00;
  }

  float gyroY_temp = g.gyro.y;
  if(abs(gyroY_temp) > gyroYerror)
  {
    gyroY += gyroY_temp/70.00;
  }

  float gyroZ_temp = g.gyro.z;
  if(abs(gyroZ_temp) > gyroZerror)
  {
    gyroZ += gyroZ_temp/90.00;
  }
  // For debugging purposes
  // Serial.println(gyroX); 
  // Serial.println(gyroY); 
  // Serial.println(gyroZ); 
  // delay(500);
}
/************************************************************************/
/*                 Gathering data of Accelerometer                      */
/************************************************************************/
void getAccReadings()
{
  mpu.getEvent(&a, &g, &temp);
  
  //Get the current acceleration values
  accX = a.acceleration.x;
  accY = a.acceleration.y;
  accZ = a.acceleration.z;

  // For debugging purposes
  // Serial.println(accX); 
  // Serial.println(accY); 
  // Serial.println(accZ); 
  // Serial.println("\n");
  // delay(500);
}
/************************************************************************/
/*               Gathering data of Flex Resistances                     */
/************************************************************************/
void getFlexReadings()
{
  float Flex_Value1 = analogRead(Flex_Sensor1);
  float Flex_Value2 = analogRead(Flex_Sensor2);
  float Flex_Value3 = analogRead(Flex_Sensor3);
  float Flex_Value4 = analogRead(Flex_Sensor4);
  float Flex_Value5 = analogRead(Flex_Sensor5);

  flexV1 = Flex_Value1 * VCC / 4095.0;
  flexR1 = R_Divider * (VCC / flexV1 - 1.0);

  flexV2 = Flex_Value2 * VCC / 4095.0;
  flexR2 = R_Divider * (VCC / flexV2 - 1.0);

  flexV3 = Flex_Value3 * VCC / 4095.0;
  flexR3 = R_Divider * (VCC / flexV3 - 1.0);

  flexV4 = Flex_Value4 * VCC / 4095.0;
  flexR4 = R_Divider * (VCC / flexV4 - 1.0);

  flexV5 = Flex_Value5 * VCC / 4095.0;
  flexR5 = R_Divider * (VCC / flexV5 - 1.0);

  //  Serial.println(flexR1); 
  //  Serial.println(flexR2); 
  //  Serial.println(flexR3); 
  //  Serial.println(flexR4); 
  //  Serial.println(flexR5); 
  //  Serial.println("\n");
  //  delay(500);
}
/************************************************************************/
/*       Fixing the multiple printing of the same gestures              */
/************************************************************************/
boolean printGestureReadings()
{
  if (!OldstoreReadings.equals(storeReadings))
  {
    OldstoreReadings = storeReadings;
    return true;
  }
  return false;
}
/************************************************************************/
/*                              Datasets                                */
/************************************************************************/
void getGestureReadings()
{
  if (flexR1>=3000 && flexR1<=8500 && flexR2>=3000 && flexR2<=8500 && flexR3>=3000 && flexR3<=8500 && flexR4>=3000 && flexR4<=8500 && flexR5>=3000 && flexR5<=8500)
  {
    storeReadings = "IDLE";
  }
  if(flexR1>=7000 && flexR1<=18000 && flexR2>=3000 && flexR2<=7000 && flexR3>=7000 && flexR3<=18000 && flexR4>=7000 && flexR4<=18000 && flexR5>=7000 && flexR5<=18000)
  {
    storeReadings = "1";
  }
  if(flexR1>=7000 && flexR1<=18000 && flexR2>=3000 && flexR2<=7000 && flexR3>=3000 && flexR3<=7000 && flexR4>=7000 && flexR4<=18000 && flexR5>=7000 && flexR5<=18000)
  {
    storeReadings = "2";
  }
  if(flexR1>=3000 && flexR1<=7000 && flexR2>=3000 && flexR2<=7000 && flexR3>=3000 && flexR3<=7000 && flexR4>=7000 && flexR4<=18000 && flexR5>=7000 && flexR5<=18000)
  {
    storeReadings = "3";
  }
   if(flexR1>=3000 && flexR1<=7000 && flexR2>=3000 && flexR2<=7000 && flexR3>=7000 && flexR3<=18000 && flexR4>=7000 && flexR4<=18000 && flexR5>=3000 && flexR5<=8500)
  {
    storeReadings = "I LOVE YOU!";
  }
  if(flexR1>=3000 && flexR1<=7000 && flexR2>=7000 && flexR2<=18000 && flexR3>=7000 && flexR3<=18000 && flexR4>=7000 && flexR4<=18000 && flexR5>=3000 && flexR5<=8500)
  {
    storeReadings = "Name";
  }
  if(accX<=(-3.50) && accX>=(-10.50))
  {
    storeReadings = "My!";
  }
   if(accX>=(5.50) && accX<=(10.50))
  {
    storeReadings = "HELLO!";
  }
  if (printGestureReadings())
  {
       Serial.print(storeReadings + "\n");
  }
  // Sends the value only to client ajax request
  server.send(200, "text/plane", storeReadings); 
}
/************************************************************************/
/*                              Setup                                   */
/************************************************************************/
void setup() 
{
  Serial.begin(115200);
  pinMode(LED, OUTPUT);
  initMPU();
  Calibration();
  initWiFi();

  server.on("/", handleRoot); //This is diplay page
  // To get update for gesture reading only
  server.on("/read_gesture", getGestureReadings); 
  server.begin();
  Serial.println("HTTP server started!\n");
  digitalWrite(LED, HIGH);
}
/************************************************************************/
/*                              Loop                                    */
/************************************************************************/
void loop() 
{
  getGyroReadings();
  getAccReadings();
  getFlexReadings();
  getGestureReadings();
  server.handleClient();
  delay(500);
}
/************************************************************************/
